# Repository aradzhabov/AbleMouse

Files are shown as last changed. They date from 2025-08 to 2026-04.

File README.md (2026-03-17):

# AbleMouse Ecosystem 

> English | [Chinese](README.cn.md) | [Russian](README.ru.md) | 🌍 Help us translate! Make the project global.

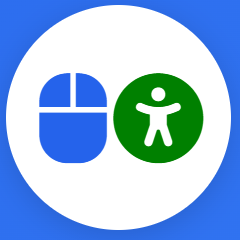
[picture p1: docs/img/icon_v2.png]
AbleMouse Demo
[//]: # ( )

## ✨ Open-source alternative to solutions like **MouthPad**, **eye-trackers**, or even complex systems like **Neuralink**.

> ❤️Our solution gives people with physical disabilities the power to go online — and in doing so, rediscover their self-worth, confidence, and dignity.

> [AbleMouse was selected by the ✨Product Hunt (PH) editors and received the "Featured" status. This is a significant honor. It means the world to me that people voted with their hearts.](https://www.producthunt.com/products/ablemouse-control-with-tongue-or-touch/launches)

### 🚀 [News]
>
   > AbleMouse now consists of several sub-products designed to assist users [based on their individual physical abilities](#product-compatibility-with-user-physical-abilities).
> 
> 🔥 Jan 2026  - [AbleMouse Beyond Switch](AbleMouse_Beyond_Switch_edition.md) - Control your entire PC with a single gesture. A uniquely simple approach.
> 
   > December 2025 - [AbleMouse AI Edition](AbleMouse_AI_edition.md)  is introduced. Cursor control using computer vision!
> 
   > November 2025 - [MouseCommander (win)](https://github.com/aradzhabov/AbleMouse/blob/main/src/windows/auto_hot_key/README.md) is introduced. Mouse Gesture-Controlled Quick Actions. +  [A new 3D-printable case for the ESP32 board is available](https://github.com/aradzhabov/AbleMouse/blob/main/AbleMouseDIY.md#news--november-27-2025)
> 
   > September 2025 - [AbleMouse DIY Edition](AbleMouseDIY.md) is introduced. Control your mouse with just tongue movements or simple touches on fully customizable pedals with any available body part. 
> 
---

# Product Compatibility with User Physical Abilities

> 🛈 AbleMouse now consists of several sub-products designed to assist users based on their individual physical abilities. Below is a table to help you navigate the available options and find the most suitable one for your needs. Each product name includes a link to its dedicated page with detailed information.

| User's Physical Challenge                                | Usable Body Part(s)                                   | Recommended Product                                                                                                                                          | Release Status    | Compatible Operating Systems                                                      |
|----------------------------------------------------------|-------------------------------------------------------|--------------------------------------------------------------------------------------------------------------------------------------------------------------|-------------------|-------------------------------------------------------------------------------------|
| Complete paralysis of body and head                      | Can use tongue                                        | **[AbleMouse DIY Edition](AbleMouseDIY.md)**                                                                                                                 | Already available | Windows, macOS, iOS, iPadOS, Unix (Ubuntu), Android                                |
| Complete paralysis of body and head                      | Imagine a person who is completely paralyzed (both body and head) and is also unable to speak. In the specific case I am referring to, the individual only had access to a single micro-movement — he could only slightly open his mouth.                                                  | **[AbleMouse Beyond Switch edition](AbleMouse_Beyond_Switch_edition.md)**                                                                                                                      | 🔥Jan 2026        | Windows                                                                             |
| Complete body paralysis                                  | Can tilt, turn, or nod head; eyes or mouth functional | **[AbleMouse AI Edition](AbleMouse_AI_edition.md)**                                                                                                          | Already available | Windows, macOS (Unix/Ubuntu support possible — requires testing)                   |
| Poor head control (e.g., due to cerebral palsy)          | Can move other body parts (even imprecisely)          | **[AbleMouse DIY Edition](AbleMouseDIY.md)**                                                                                                                 | Already available | Windows, macOS, iOS, iPadOS, Unix (Ubuntu), Android                                |
| Any of the above conditions                              | —                                                     | **[MouseCommander (win)](https://github.com/aradzhabov/AbleMouse/blob/main/src/windows/auto_hot_key/README.md) as an additional tool to any above products** | Already available | Windows                                                                             |

## Who Is It For?
> This solution is designed for users who, for various reasons, are unable to operate a mouse effectively.
- People with **ALS** (Amyotrophic Lateral Sclerosis), cerebral palsy, spinal cord injuries, muscular dystrophy
- Those undergoing **rehabilitation after stroke**
>...and for those who want to help.
- **Parents, teachers, and activists** who want to provide affordable help
- Anyone who believes **assistive technology should be a right, not a privilege**

## How to Contribute

We welcome contributions! Here's how you can help:

1. **Spread the Word** - Share with communities who might benefit
2. **Improve Documentation** - Help make guides clearer and more accessible. Help translate to make this project available to non-English speakers.
3. **Develop Features** - Implement new functionality or platform support
4. **Test and Report** - Try building and report any issues

## Support
- aradzhabov@gmail.com
- [LinkedIn](https://www.linkedin.com/in/aradzhabov/)

## License

MIT License - see [LICENSE](LICENSE) file for details.

---

### Connect With Us



**#Accessibility #AssistiveTech #OpenSource #DIY #Innovation #MouthPad #eye-tracker #Neuralink**

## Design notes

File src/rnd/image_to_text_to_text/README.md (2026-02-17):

# talk2cam: Ask Your Camera Anything. Completely locally

**Live Camera Feed QA. Vision-to-Text: Conversing with Reality in Real-Time**




>▶️[Video talk2cam](https://youtu.be/8lIvBt9HPiM)
---

## Special Thanks
Special thanks to the **[Alibaba Cloud team](https://www.alibabacloud.com/)** for supporting the [AbleMouse project](https://github.com/aradzhabov/AbleMouse/tree/main), which helps make the world more accessible for people with disabilities, and of course for their excellent open-weight models.

---

## About The Project

I've been experimenting with integrating vision-capable language models with live camera streams. The result? An interactive system that can:

- Process real-time video frames
- Answer natural language questions about the scene
- Adapt to new instructions on the fly

This opens up possibilities for:
- 👁️ Assistive technology for visually impaired
- 🏠 Real-time scene understanding
- 🤝 Interactive AI companions
- 📹 Smart surveillance systems

---

## 🚀 How to Run

### 1. Install [llama.cpp](https://github.com/ggml-org/llama.cpp)

There are multiple ways to do this. The simplest is to download a pre-compiled version for your hardware.

For example, I downloaded from [llama.cpp releases](https://github.com/ggml-org/llama.cpp/releases):
- `Windows x64 (CUDA 12)`
- `CUDA 12.4 DLLs`

- **Note 1:** Check your CUDA version by running `nvidia-smi` and looking at the top right corner.
- **Note 2:** If using GPU, copy files from `CUDA 12.4 DLLs` into the `Windows x64 (CUDA 12)` folder.
- **Note 3:** Without GPU everything still works, but you'll need to set a 10+ second delay between frames (for larger models).

### 2. Choose a Model

Browse video-text-to-text models with GGUF format on Hugging Face:
👉 [Video-to-Text Models with llama.cpp support](https://huggingface.co/models?pipeline_tag=video-text-to-text&library=gguf&apps=llama.cpp&sort=downloads)

**You don't need to manually download models** - when you run llama-server, it will automatically download the specified model.

### 3. Start the Server

#### Without GPU: 
- llama-server -hf prithivMLmods/SAGE-MM-Qwen2.5-VL-7B-SFT_RL-GGUF:Q4_K_M

#### With GPU:

- llama-server -hf prithivMLmods/SAGE-MM-Qwen2.5-VL-7B-SFT_RL-GGUF:Q4_K_M -ngl 99

Why this model? I like this model because it's multilingual and answers questions very well.
👉 [SAGE-MM-Qwen2.5-VL-7B-SFT_RL-GGUF](https://huggingface.co/prithivMLmods/SAGE-MM-Qwen2.5-VL-7B-SFT_RL-GGUF) on Hugging Face

💻 For weaker computers:
Try this smaller model (I found it good at describing what it sees, but not as good at answering follow-up questions):
llama-server -hf ggml-org/SmolVLM2-500M-Video-Instruct-GGUF:Q8_0

👉 [SmolVLM2-500M-Video-Instruct-GGUF](https://huggingface.co/ggml-org/SmolVLM2-500M-Video-Instruct-GGUF)
 
### 4. Run Camera Llama
[talk2cam.py](./talk2cam.py)

How to Use
- Start - Click "▶ Start" to begin camera capture
- Ask - Type your question in the instruction box
- Settings - Click "⚙ Settings" to adjust server URL, image size, and interval

⚙️ Configuration Options
- Server URL	Where llama.cpp server is running (default: http://localhost:8080)
- Camera ID	Which camera to use (0 = built-in, 1 = external)
- Interval	Milliseconds between frame captures
- Image Size	Resize images before sending (smaller = faster)
- Instruction	What to ask the model about each frame

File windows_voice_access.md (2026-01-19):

### Enabling Voice Access

1. Go to Windows **Settings > Accessibility > Speech**.
2. Toggle the **Voice access** switch to **On**.

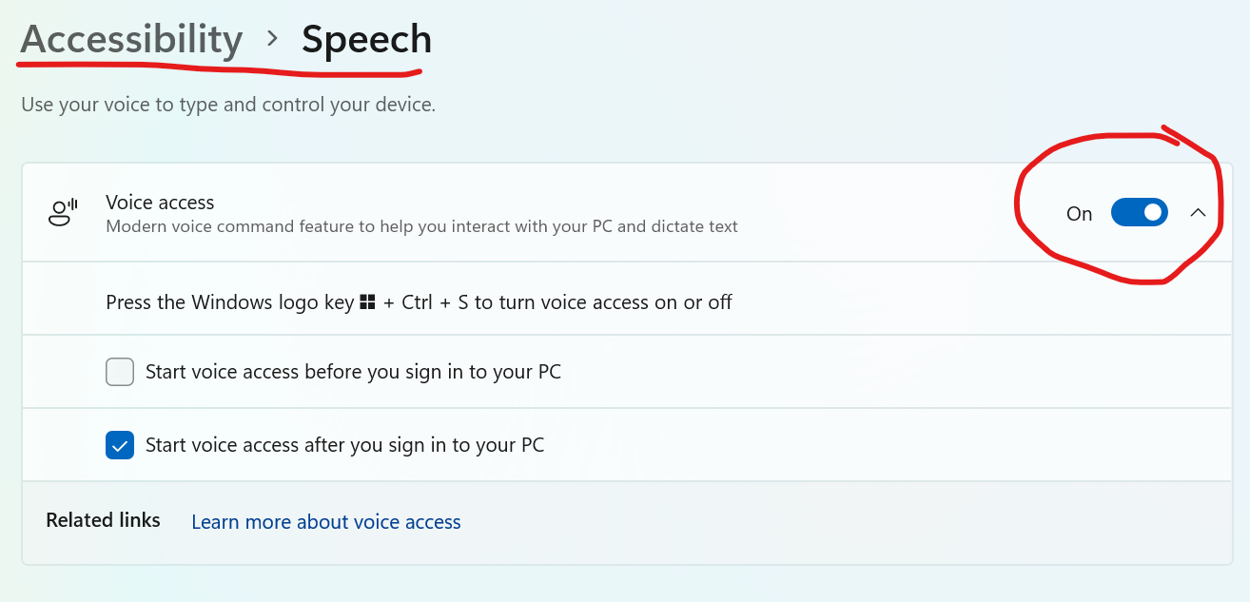
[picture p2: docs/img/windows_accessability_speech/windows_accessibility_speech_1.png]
Voice Access Settings


### Configuring Audio Input

Once enabled, the Voice Access bar will appear at the top of your screen. To route the audio correctly, follow these steps:

1. Click on the **Settings** (gear icon) on the Voice Access bar.
2. Under **Select default microphone**, choose **CABLE Output (VB-Audio Virtual Cable)**.
3. Finally, switch the mode from **Sleep** to **Active** by clicking the microphone icon on the left side of the bar.

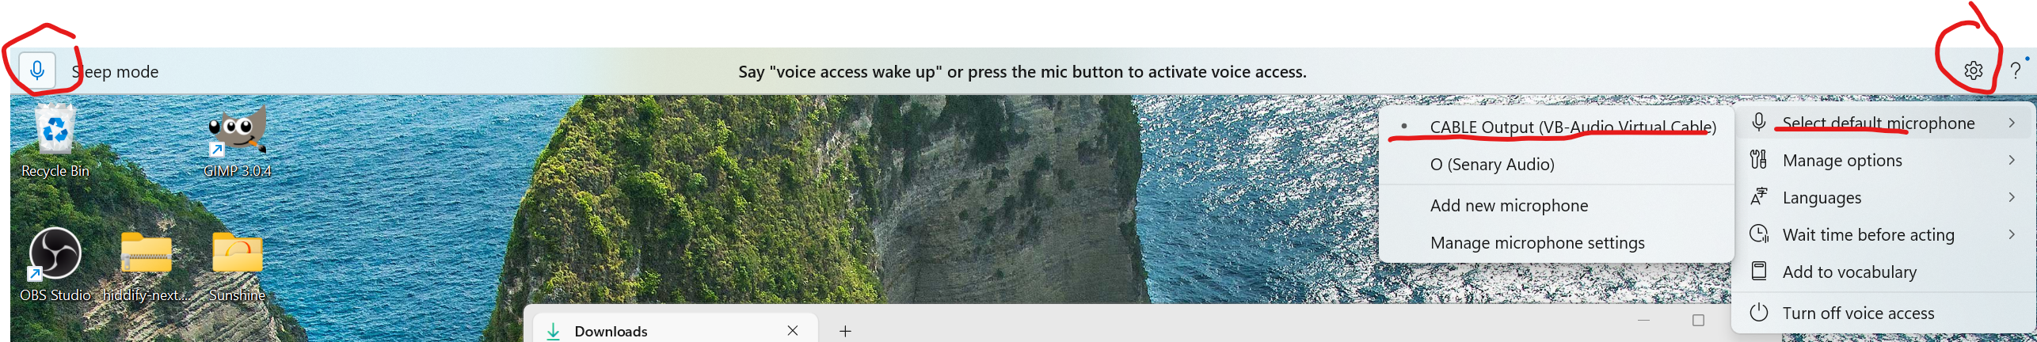
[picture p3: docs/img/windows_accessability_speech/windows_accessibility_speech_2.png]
Voice Access Configuration


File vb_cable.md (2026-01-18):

# VB-Cable Installation and Setup

> **Note:** VB-CABLE is distributed as  ([**Donationware**](https://vb-audio.com/Services/licensing.htm)). While it is free to download and use for personal purposes, a donation or license purchase is expected if you find the software useful or use it professionally. You can support the developer directly at the [VB-Audio Webshop](https://shop.vb-audio.com/en/win-apps/11-vb-cable.html).

### Why is this required?
VB-CABLE is a important component that allows the audio commands sent by the server to reach the **Windows Speech Control**. Without this setup, the system will "play" the audio, but Windows will not "hear" it as an input command.

---

### Step-by-Step Instructions

#### 1. Download and Install
* Download the driver pack: **VBCABLE_Driver_Pack45.zip** at [vb-audio.com/Cable/](https://vb-audio.com/Cable/).
* Extract the archive, run the setup as Administrator, and install.
* **Restart your computer** to complete the installation.

#### 2. Set Default Output
* Go to Windows **Settings > System > Sound**.
* In the **Output** section, select **CABLE Input (VB-Audio Virtual Cable)** as your output device.

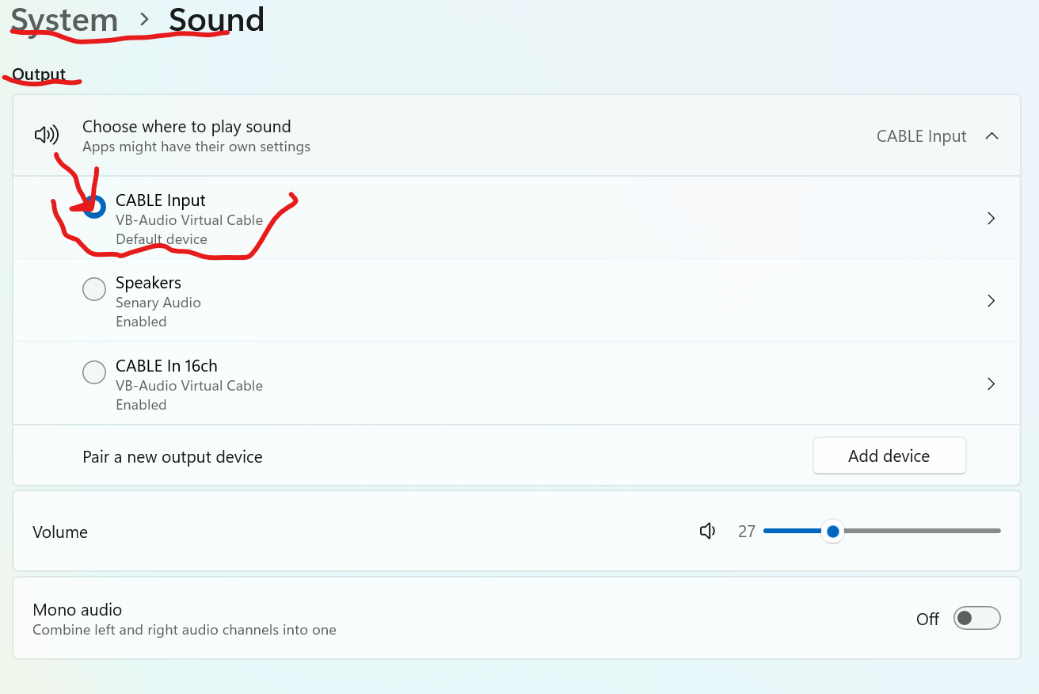
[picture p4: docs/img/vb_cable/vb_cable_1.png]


#### 3. Open Advanced Sound Settings
* Scroll down and click on **More sound settings** (or Sound Control Panel).

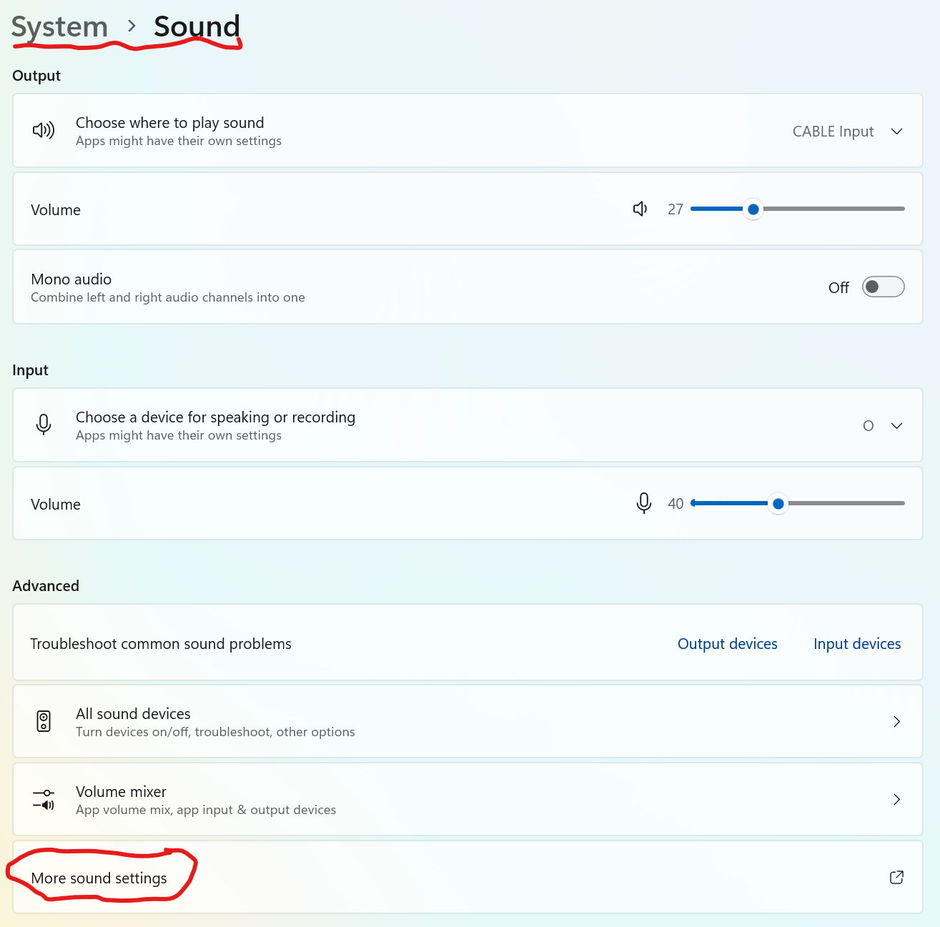
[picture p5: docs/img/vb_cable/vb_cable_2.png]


#### 4. Configure Audio Routing (Loopback)
* Switch to the **Recording** tab.
* Right-click on **CABLE Output** and select **Properties**.
* In the new window, go to the **Listen** tab.
* Check the box: **"Listen to this device"**.
* In the dropdown list under "Playback through this device", select the **speakers or headphones** you normally use for audio.

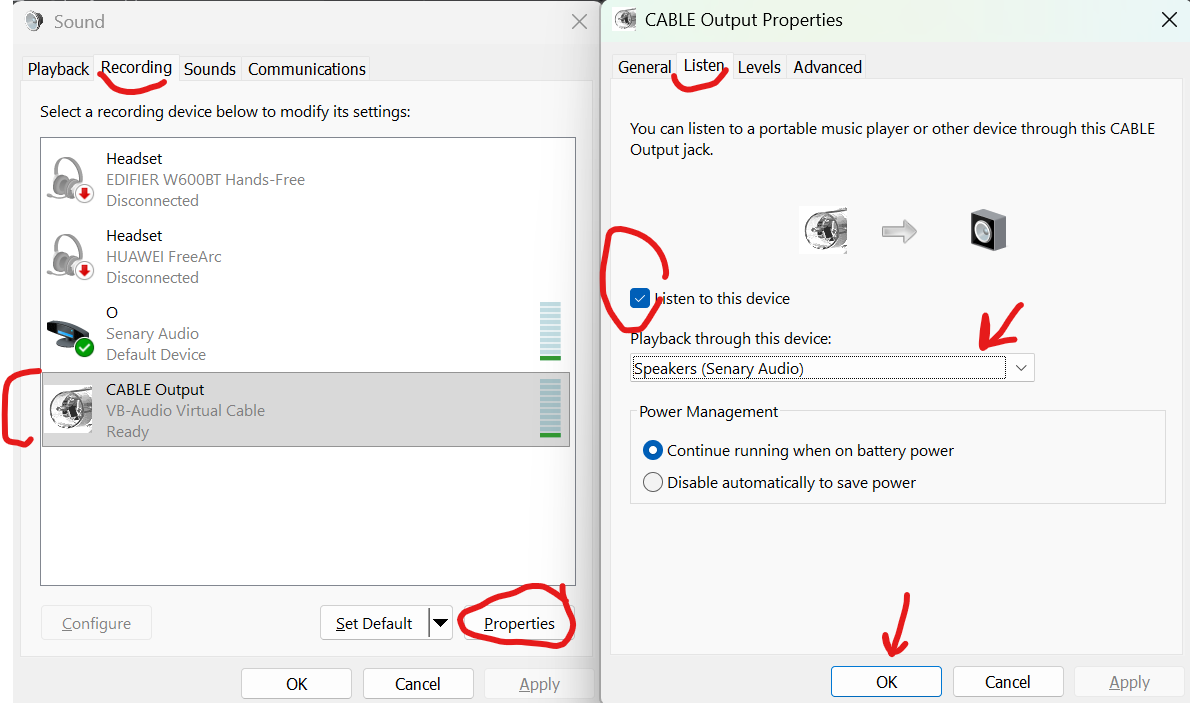
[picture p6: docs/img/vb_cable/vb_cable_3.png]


---

### Result
After following these steps, any audio played by the system will be routed through **VB-CABLE**, allowing Windows to "hear" and process the played commands.

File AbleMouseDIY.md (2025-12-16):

# AbleMouse DIV edition

> ❤️Control your mouse with just tongue movements or simple touches on fully customizable pedals with any available body part.
High-precision & affordable: the DIY (do it yourself) assistive solution

>▶️[Video AbleMouse](https://youtu.be/1eeg7Sakj_I)

### Assembly Steps
> [English](docs/en/assemble-guide.md) | 🌍 Help us translate! Make the project global.

## News  (November 27, 2025)
AbleMouse expands support to Unix, iOS, & iPadOS, making it compatible with all major OSes.
[A new 3D-printable case for the ESP32 board is available.](https://github.com/aradzhabov/AbleMouse/tree/main/3d_printer/models/esp32_box/variations/1)
The project also introduces [MouseCommander (win)](https://github.com/aradzhabov/AbleMouse/blob/main/src/windows/auto_hot_key/README.md), a new open-source component. It solves a key problem: how to use keyboard shortcuts and system tools without a physical keyboard or standart mouse. It opens a customizable menu via a gesture, enabling features like instant cursor "teleportation" via a screen preview, an on-screen keyboard and more.

## Key Features

| Feature | Description                                                                                                                                                                                                                                                                                                                |
|---------|----------------------------------------------------------------------------------------------------------------------------------------------------------------------------------------------------------------------------------------------------------------------------------------------------------------------------|
| **Universal Accessibility** | Helps both completely immobile users and those with minimal motor skills. You can use our solution with just your tongue, even with total paralysis.                                                                                                                                                                       |
| **Wireless Freedom** | Full Bluetooth control without cables                                                                                                                                                                                                                                                                                      |
| **Multi-Platform Support** | Works on Windows, macOS, iOS, iPadOS, unix(Ubuntu) and Android                                                                                                                                                                                                                                                             |
| **Plug & Play Simplicity** | For Windows, macOS, iOS, iPadOS, unix(Ubuntu) end-users: No additional software or drivers are required. Simply find and connect our device using your computer's standard Bluetooth settings—just like pairing a pair of wireless headphones. The moment it's connected, you can begin controlling your mouse.                                    
| **Ultra-Low Cost** | All components cost less than $10 USD                                                                                                                                                                                                                                                                                      |
| **Short Learning Curve** | The adaptation was startlingly fast—within 20 minutes, my control was precise and confident                                                                                                                                                                                                                                |
| **Open Source & hackable** | DIY. Assemble and customize it yourself in a garage, workshop, or makerspace. All instructions and code are openly available.                                                                                                                                                                                              
| **No Expert Needed** | You don't need to be an IoT expert to build it. In fact, the setup is so simple that you can easily find a helper in your immediate circle—be it a colleague from the IT department, a tech-savvy friend, or a student. It's all based on simple copy-paste operations, so no deep knowledge is required from them either. 

## Support
- aradzhabov@gmail.com
- [LinkedIn](https://www.linkedin.com/in/aradzhabov/)

## License

MIT License - see [LICENSE](LICENSE) file for details.

---

### Connect With Us



**#Accessibility #AssistiveTech #OpenSource #DIY #Innovation #MouthPad #eye-tracker #Neuralink**

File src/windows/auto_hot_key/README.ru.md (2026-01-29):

# MouseCommander — Быстрые действия, управляемые жестами мыши

> Этот подход был разработан в ответ на запросы людей с ограниченными возможностями, использующих Windows, чтобы упростить и ускорить их рабочий процесс. Он специально предназначен для тех, кто может управлять только указателем мыши (без использования обычной мыши) и не может пользоваться клавиатурой. Решение позволяет быстро перемещаться к нужным точкам экрана, вызывать экранный клавиатуру (OSK) и позиционировать курсор внутри неё, а также упрощает наведение на конкретные точки с помощью прицельной сетки.
> 
> Подход легко переводится на любой язык и расширяется дополнительными функциями по мере необходимости.
> 
> Ниже приведён подробный рабочий пример скрипта. Используя его как основу, вы можете разработать собственный жест и персонализированный набор доступных команд, которые наилучшим образом соответствуют вашим потребностям.

## Обзор
> ▶️ [пример вызова меню при использовании AbleMouse AI edition](https://rutube.ru/video/c27362a9037dbe7b9ceb7fb06f275b4c/?r=wd&t=69)
> 
> ▶️ [демонстрация возможностей](https://rutube.ru/video/83b28184f3693f3217fb0cab863da98a/)
> 
Скрипт автоматизации на основе жестов, распознающий движения мыши (влево → вправо) как пример для отображения панели быстрого доступа с различными системными функциями.

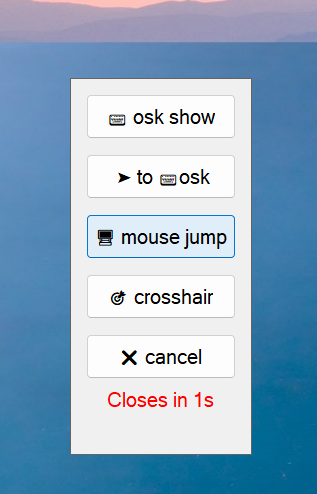
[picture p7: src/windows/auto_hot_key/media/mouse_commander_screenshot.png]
Скриншот


## Исходный код
[mouse_commander.ahk](./mouse_%D1%81ommander.ahk)

## Возможности
- Распознавание жестов мыши (движение влево → вправо)
- Панель быстрого доступа с настраиваемыми действиями
- **osk hide/show**: Переключение видимости экранный клавиатуры
- **osk to cursor**: вызов экранной клавиатуры и фокусировка курсора на ней
- **mouse jump**: Мгновенный переход указателя мыши в любую точку рабочего стола
- **crosshair**: Переключение прицельной сетки поверх экрана
- Возможность самостоятельно добавлять новые функции

## Настройки конфигурации

### Параметры жестов
```autohotkey
gestureTimeWindow := 1000  ; Временное окно распознавания жеста в миллисекундах
minDistance := 50          ; Минимальное расстояние перемещения в пикселях
maxPause := 300            ; Максимальная пауза между движениями
menuTimeout := 3000        ; Автозакрытие меню через 3 секунды
```

### Настройки горячих клавиш
```
oskToggleHotkey := "#^o"   ; Win+Ctrl+O — переключение видимости экранных клавиатур
mouseJumpHotkey := "#+d"   ; Win+Shift+D
crosshairHotkey := "#!p"   ; Win+Alt+P
```

### Установка (протестировано с AutoHotkey v2.0 и PowerToys 0.94)

```
Установите AutoHotkey v2.0
Установите PowerToys 0.94
Сохраните скрипт с расширением .ahk
Запустите скрипт
```

### Использование

```
Базовый жест
Выполните движение мыши ВЛЕВО (> 50 пикселей)
Немедленно выполните движение ВПРАВО (> 50 пикселей)
Весь жест должен быть завершён в течение 1000 мс
```

### Опции панели быстрого доступа
```
osk hide/show: Переключение видимости экранных клавиатур
osk to cursor: Перемещение экранных клавиатур к курсору и фокусировка
mouse jump: Мгновенный переход указателя мыши в любую точку экрана
crosshair: Переключение прицельной сетки
Cancel: Закрыть меню
```

### Примечания
```
Скрипт автоматически определяет, запущена ли экранные клавиатуры
Все элементы интерфейса корректно уничтожаются для предотвращения утечек памяти
```

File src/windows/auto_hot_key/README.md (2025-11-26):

# MouseCommander - Mouse Gesture-Controlled Quick Actions

>This approach was developed in response to requests from people with disabilities who use Windows, to simplify and accelerate their workflow. It is especially designed for those who can only control a mouse pointer (without a regular mouse) and cannot use a keyboard. It enables quick movement to desired screen locations, calling the on-screen keyboard (OSK) and positioning the cursor within it, and simplifies aiming at specific points using crosshair assistance.
This approach can be easily extended with additional functions as needed.
> 
> Below is a detailed working example of a script. Using this as a foundation, you can design a custom gesture and a personalized set of available commands that best suit your needs.

## Overview
>▶️[demo](https://youtu.be/IWix3twlcew)
> 
A gesture-based automation script that recognizes mouse gestures (Left → Right) as an example to display a quick access panel with various system functions.



## Source
[mouse_commander.ahk](./mouse_сommander.ahk)

## Features
- Mouse gesture recognition (Left → Right movement)
- Quick access panel with customizable actions
- osk hide/show: Toggle on-screen keyboard visibility
- osk to cursor: Move OSK to cursor position and focus it
- mouse jump: Jump the mouse pointer quickly to anywhere on your desktop.
- crosshair: Toggle crosshair overlay
- you can add new features by yourself

## Configuration Settings

### Gesture Settings
```autohotkey
gestureTimeWindow := 1000  ; Gesture time window in milliseconds
minDistance := 50          ; Minimum movement distance in pixels
maxPause := 300            ; Maximum pause between movements
menuTimeout := 3000        ; Menu close timeout after 3 seconds
```

### Hotkey Settings
```autohotkey
oskToggleHotkey := "#^o"   ; Windows+Ctrl+O - toggles OSK visibility
mouseJumpHotkey := "#+d"   ; Windows+Shift+D
crosshairHotkey := "#!p"   ; Windows+Alt+P
```

## Installation (tested with AutoHotkey v2.0 and PowerToys 0.94)
1. Install [AutoHotkey v2.0](https://www.autohotkey.com/)
2. Install [PowerToys 0.94](https://github.com/microsoft/PowerToys/releases/tag/v0.94.0)
2. Save the script with `.ahk` extension
3. Run the script

## Usage

### Basic Gesture
1. Make a LEFT mouse movement (> 50px)
2. Immediately follow with a RIGHT movement (> 50px)
3. The entire gesture must be completed within 1000ms

### Quick Panel Options
- **osk hide/show**: Toggle on-screen keyboard visibility
- **osk to cursor**: Move OSK to cursor position and focus it
- **mouse jump**: Jump the mouse pointer quickly to anywhere on your desktop.
- **crosshair**: Toggle crosshair overlay
- **Cancel**: Close the menu

### Additional Controls
- **Pause**: Toggle gesture tracking on/off
- **Ctrl+Alt+I**: Show information panel
- **Escape**: Close active GUI window

## Technical Details

### Gesture Recognition
The script uses a state machine to track mouse movements:
- State 0: Waiting for initial movement
- State 1: Left movement detected
- State 2: Right movement completes the gesture

### Feedback System
- Visual tooltips provide gesture status feedback
- Countdown timer shows menu auto-close timing
- Color-coded indicators (gray → red) for time remaining

### GUI Management
- Always-on-top tool window
- Borderless design with custom styling
- Automatic positioning near cursor
- Timeout-based auto-destruction

## Customization
Modify the configuration section to:
- Adjust gesture sensitivity (`minDistance`, `maxPause`)
- Change menu timeout duration (`menuTimeout`, `countdownTime`)
- Customize hotkey combinations
- Add new menu options and corresponding functions

## Notes
- The script automatically detects if OSK is already running
- All GUI elements are destroyed properly to prevent memory leaks
- The pause feature allows temporary disabling of gesture recognition

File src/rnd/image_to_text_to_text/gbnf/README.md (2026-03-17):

* Ограничиваю модель двумя предложениями через настройки сервера
>llama-server -hf prithivMLmods/SAGE-MM-Qwen2.5-VL-7B-SFT_RL-GGUF:Q4_K_M -ngl 99 --grammar-file two_sentences.gbnf

>

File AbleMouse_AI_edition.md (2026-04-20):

# AbleMouse AI edition

> ❤️Control the mouse pointer using your face.
> 
> The code works under both Windows and Mac Os. Note: Unix/Ubuntu support possible — requires testing

>▶️[Video AbleMouse AI edition](https://youtu.be/AlqSVKt535Y)
> / [Source Code](src/ablemouse_ai_edition/able_mouse_ai_edition.py) / ▶️[initial setup](https://youtu.be/KCn4GMMQkxc)
> 
> Note: In the video demonstration for calling the on-screen keyboard in Windows, I used gesture recognition via [MouseCommander (win)](https://github.com/aradzhabov/AbleMouse/blob/main/src/windows/auto_hot_key/README.md) , which is also part of the AbleMouse project. <br> On macOS, there is no need to use MouseCommander, as the built-in keyboard with the "dwelling" setting enabled and customizable transparency levels is both convenient and does not clutter the interface with its presence.

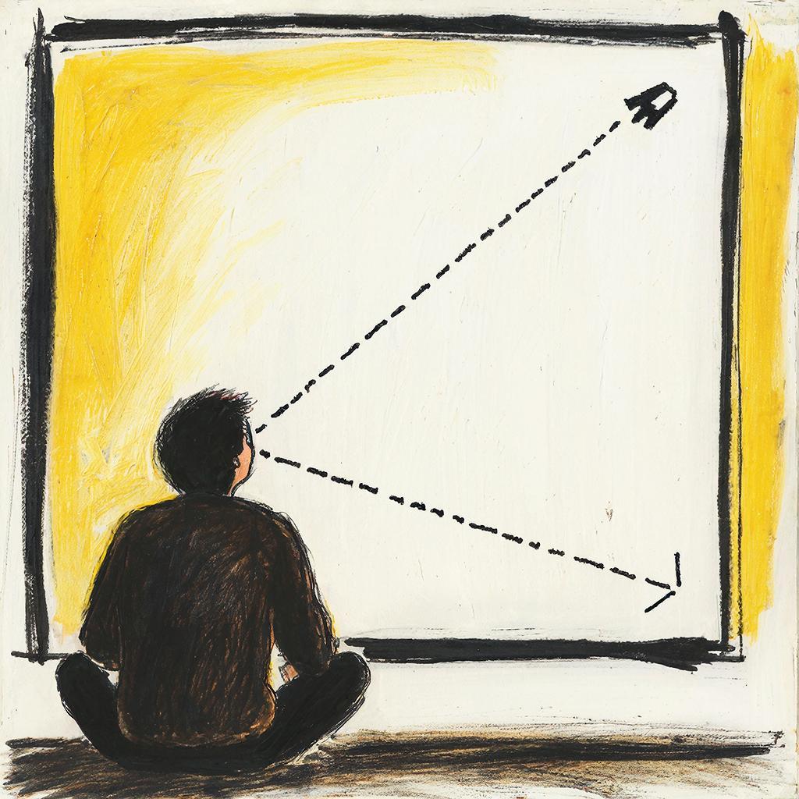
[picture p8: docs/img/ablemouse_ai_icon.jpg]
AbleMouse AI edition


An important aspect is that the solution is fully open-source and can be easily adapted to meet the needs of a specific individual.

To use AbleMouse AI edition, it is enough that you can turn and tilt your head, and use your eyes and mouth. 
The mouse pointer is positioned based on the direction of your nose, allowing you to work effectively even with very large screens.
macOS and Windows do not have such a solution built-in.
Another very important difference from other solutions is that your eyes remain free, as the tracking is based on the direction of your nose. This provides a much more natural feeling for us as humans. For example, solutions that require you to look at the point where you want to move the cursor demand significantly more effort and feel unnatural. An ordinary person using a hand-operated mouse can look anywhere—AbleMouse allows you to do the same.

A few notes on use and configuration:

*   To adapt the program for a specific person, you will need the assistance of someone with basic Python knowledge. In my opinion, a school student's level is sufficient.
    The solution itself is very simple and essentially consists of a single file where settings need to be adjusted for the specific user. Most parameters in the code are self-explanatory from their names, and in most cases, many of them do not need to be changed. I will describe the most important ones below. Please don't hesitate to write to me if you have any questions.

*   I recommend using an external webcam, as this allows for maximum comfort in screen positioning, especially for bedridden individuals.
    If you are using an external webcam, you need to set the `camera` parameter to a value other than 0 (usually this value is 1). The value 0 corresponds to the built-in camera in your laptop.

All camera settings are located in `able_mouse_ai_edition_config.json` under the `"main"` section:

```json
"main": {
    "camera": 0,
    ...
}   
```

*   `EYE_CLOSE_THRESHOLD` - Thresholds for determining closed eyes (distance between the upper and lower eyelashes).
    `MOUTH_OPEN_THRESHOLD` - Threshold for determining an open mouth (distance between the lips).
 
```commandline
"eye_and_mouth": {
    "eye_close_threshold": 0.005,
    "mouth_open_threshold": 0.004,
    ...
}

```

It is important to understand that these parameters greatly depend on the distance of the face from the camera and the camera itself. You also need to consider that, for example, when you tilt your head, the distance between the calculated points decreases due to projection. When you run the program, you can easily check its operation with your settings, as a window will open displaying each gesture. This window can also be used for training. The window will remain open while the program is running but can be hidden behind other applications. This does not affect the program's operation.

*   For Python developers: `Python 3.9-3.12`. To run the program, you will need to create a virtual environment (venv) and install just 3 packages:
    `opencv-python`, `mediapipe==0.10.21`, `pyautogui`
    After that, run [able_mouse_ai_edition.py](src/ablemouse_ai_edition/able_mouse_ai_edition.py). !!After launching, don't forget to properly [calibrate the camera position](https://youtu.be/KCn4GMMQkxc)!!

*   Overall, I also see the program as an educational moment. I think many students will be able to pick up something useful for themselves.
    The program itself is a maximally simplified, small slice from my R&D version from two years ago.

    I could have significantly simplified the code by using `sleep` instructions in more places instead of cooldowns, but my experience shows that these freezes are very noticeable and feel unnatural. I also intentionally did not publish a clean object-oriented version of the code, as it will be much easier for beginners to understand a version without OOP.

## Support
- aradzhabov@gmail.com
- [LinkedIn](https://www.linkedin.com/in/aradzhabov/)

## License

MIT License - see [LICENSE](LICENSE) file for details.

---

### Connect With Us



**#Accessibility #AssistiveTech #OpenSource #DIY #Innovation #MouthPad #eye-tracker #Neuralink**

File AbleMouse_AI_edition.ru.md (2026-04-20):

# AbleMouse AI edition

> ❤️ Управление курсором мыши с помощью лица. В точку по направлению, куда указывает нос, позиционируется курсор, а клики делаются глазами и ртом. Позиционирование происходит именно по направлению, т.е. экран может быть любого размера, но человеку никуда не нужно двигаться - нужно просто направить нос в точку, куда переместить курсор.
> 
> Код работает в Windows и macOS. Примечание: поддержка Unix/Ubuntu возможна, но требует тестирования.

>▶️ [Видео AbleMouse AI edition](https://rutube.ru/video/c27362a9037dbe7b9ceb7fb06f275b4c/)
> / [Исходный код](src/ablemouse_ai_edition/able_mouse_ai_edition.py) / ▶️ [Первоначальная настройка](https://youtu.be/KCn4GMMQkxc)
> 
> Примечание: В видеодемонстрации для вызова экранной клавиатуры в Windows я использовал распознавание жестов через [MouseCommander (win)](https://github.com/aradzhabov/AbleMouse/blob/main/src/windows/auto_hot_key/README.md), который также является частью проекта AbleMouse. <br> На macOS нет необходимости использовать MouseCommander, так как встроенная клавиатура с включенной функцией «ожидания» (dwelling) и настраиваемой прозрачностью очень удобна и не загромождает интерфейс.

AbleMouse AI edition

Важным аспектом является то, что это решение полностью открыто (open-source) и может быть легко адаптировано под нужды конкретного человека.

Для использования AbleMouse AI edition достаточно иметь возможность поворачивать и наклонять голову, а также задействовать глаза и рот. 
Курсор мыши позиционируется в зависимости от направления вашего носа, что позволяет эффективно работать даже с очень большими экранами. 
В macOS и Windows подобных встроенных решений нет. 

Еще одно очень важное отличие от других систем заключается в том, что ваши глаза остаются свободными, так как трекинг основан на направлении носа. Это обеспечивает гораздо более естественное ощущение для человека. Например, решения, требующие смотреть именно в ту точку, куда вы хотите переместить курсор, требуют значительно больше усилий и кажутся неестественными. Обычный человек, использующий ручную мышь, может смотреть куда угодно — AbleMouse позволяет делать то же самое.

### Несколько заметок по использованию и настройке:

*   Для адаптации программы под конкретного человека потребуется помощь кого-то с базовыми знаниями Python. На мой взгляд, уровня школьника будет достаточно. 
    Само решение очень простое и по сути состоит из одного файла, где нужно подправить настройки под конкретного пользователя. Большинство параметров в коде интуитивно понятны по их названиям, и во многих случаях их даже не придется менять. Ниже я опишу самые важные из них. Пожалуйста, не стесняйтесь писать мне, если у вас возникнут вопросы.

*   Я рекомендую использовать внешнюю веб-камеру, так как это обеспечивает максимальный комфорт в расположении экрана, особенно для лежачих больных. 
    Если вы используете внешнюю камеру, вам нужно установить параметр `camera` в значение, отличное от 0 (обычно это 1). Значение 0 соответствует встроенной камере ноутбука.

Все настройки можно изменить в  `able_mouse_ai_edition_config.json`:

```json
"main": {
    "camera": 0,
    ...
}   
```

*   `EYE_CLOSE_THRESHOLD` — пороги для определения закрытых глаз (расстояние между верхними и нижними ресницами).
    `MOUTH_OPEN_THRESHOLD` — порог для определения открытого рта (расстояние между губами).

```commandline
"eye_and_mouth": {
    "eye_close_threshold": 0.005,
    "mouth_open_threshold": 0.004,
    ...
}

Важно понимать, что эти параметры сильно зависят от расстояния лица до камеры и самой модели камеры. Также нужно учитывать, что, например, при наклоне головы расстояние между расчетными точками уменьшается из-за проекции. При запуске программы вы сможете легко проверить работу со своими настройками: откроется окно, отображающее каждый жест. Это же окно можно использовать для тренировки. Окно будет оставаться открытым во время работы программы, но его можно скрыть за другими приложениями — на работу это не влияет.

*   Для Python-разработчиков: `Python 3.9-3.12`. Для запуска программы нужно создать виртуальное окружение (venv) и установить всего 3 пакета: 
    `opencv-python`, `mediapipe==0.10.21`, `pyautogui`. 
    После этого запустите [able_mouse_ai_edition.py](src/ablemouse_ai_edition/able_mouse_ai_edition.py). !!После запуска не забудьте правильно [откалибровать положение камеры](https://youtu.be/KCn4GMMQkxc)!!

*   В целом, я рассматриваю эту программу и как образовательный момент. Думаю, многие студенты смогут почерпнуть здесь что-то полезное для себя. 
    Сама программа — это максимально упрощенный, небольшой «срез» из моей R&D версии двухлетней давности. 

    Я мог бы значительно упростить код, используя инструкции `sleep` вместо кулдаунов (cooldowns), но мой опыт показывает, что такие замирания очень заметны и ощущаются неестественно. Также я намеренно не публиковал чистую объектно-ориентированную версию кода, так как новичкам будет гораздо проще разобраться в версии без ООП.

## Поддержка
- aradzhabov@gmail.com
- [LinkedIn](https://www.linkedin.com/in/aradzhabov/)

## Лицензия

MIT License — подробности в файле [LICENSE](LICENSE).

---

### Свяжитесь с нами

[![Website](https://img.shields.io/badge/Website-Learn%20More-green)](https://aradzhabov.github.io/gagarin_data_labs/)

**#Accessibility #AssistiveTech #OpenSource #DIY #Innovation #MouthPad #eye-tracker #NeuralNetworks**

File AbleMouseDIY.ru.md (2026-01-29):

# AbleMouse DIV edition

## ✨ Проект с открытым исходным кодом — альтернатива таким решениям, как **MouthPad**, **айтрекеры**, или даже сложным системам вроде **Neuralink**.
> ❤️ Решение подойдёт для всех, кто по тем или иным причинам не может полноценно пользоваться мышью.

> Управляйте курсором мыши **движениями языка** или **простыми касаниями на полностью настраиваемые педали** любой доступной частью тела.
Высокоточное и доступное решение для ассистивных технологий, которое можно собрать своими руками (DIY).

>Мы помогаем людям с инвалидностью почувствовать себя ценными, уверенными и полноправными членами общества.

>▶️[Видеообзор AbleMouse](https://rutube.ru/video/931e70c2d8f6c1edf99c20dda61d8ad8/)
### Шаги сборки
> [Руководство по сборке](docs/ru/assemble-guide.ru.md)

## Новости (27 ноября 2025)
AbleMouse расширяет поддержку на Unix, iOS и iPadOS, становясь совместимым со всеми основными операционными системами. 
[Доступен новый корпус для платы ESP32, который можно напечатать на 3D-принтере.]((https://github.com/aradzhabov/AbleMouse/tree/main/3d_printer/models/esp32_box/variations/1))
Также в рамках проекта представлен новый компонент с открытым исходным кодом — [MouseCommander](https://github.com/aradzhabov/AbleMouse/blob/main/src/windows/auto_hot_key/README.ru.md) (для Windows). Он решает ключевую проблему: как использовать сочетания клавиш и системные инструменты без физической клавиатуры или стандартной мыши. Компонент открывает настраиваемое меню по жесту, предоставляя такие функции, как мгновенное «телепортирование» курсора с помощью предпросмотра экрана, экранную клавиатуру и многое другое.

## Ключевые особенности

| Особенность | Описание                                                                                                                                                                                                                                                                                                                                           |
|-------------|----------------------------------------------------------------------------------------------------------------------------------------------------------------------------------------------------------------------------------------------------------------------------------------------------------------------------------------------------|
| **Универсальная доступность** | Помогает как **полностью обездвиженным** пользователям, так и тем, у кого сохранены минимальные моторные навыки. Вы можете использовать наше решение даже при полном параличе, используя только язык.                                                                                                                                              |
| **Беспроводная свобода** | Полный контроль по Bluetooth без проводов                                                                                                                                                                                                                                                                                                          |
| **Поддержка нескольких платформ** | Работает на indows, macOS, iOS, iPadOS, unix(Ubuntu) и Android                                                                                                                                                                                                                                                                                     |
| **Простота Plug & Play** | Для конечных пользователей Windows, macOS, iOS, iPadOS, unix(Ubuntu): не требуется дополнительного программного обеспечения или драйверов. Просто найдите и подключите наше устройство, используя стандартные настройки Bluetooth вашего компьютера — точно так же, как вы подключаете беспроводные наушники. В момент подключения вы уже можете начать управлять курсором. |
| **Сверхнизкая стоимость** | Все компоненты стоят меньше $10 USD                                                                                                                                                                                                                                                                                                                |
| **Короткий период обучения** | Адаптация происходит поразительно быстро — (в моем случае) в течение 20 минут управление стало точным и уверенным                                                                                                                                                                                                                                  |
| **Открытый исходный код и возможность модификации** | Соберите и настройте его самостоятельно в гараже, мастерской или makerspace. Все инструкции и код открыты и доступны.                                                                                                                                                                                                                              |
| **Не нужно быть экспертом** | Вам не нужно быть экспертом в IoT, чтобы собрать его. На самом деле, setup настолько прост, что вы легко найдете помощника в своем ближайшем окружении — будь то коллега из IT-отдела, разбирающийся в технологиях друг или студент. Всё основано на простых операциях копирования-вставки, поэтому от них также не потребуется глубоких знаний.   |

## Поддержка
- aradzhabov@gmail.com
- [LinkedIn](https://www.linkedin.com/in/aradzhabov/)

## Лицензия
Лицензия MIT — подробности см. в файле [LICENSE](LICENSE).

---
### Свяжитесь с нами



**#Доступность #АссистивныеТехнологии #OpenSource #DIY #Инновации #MouthPad #Айтрекер #Neuralink**

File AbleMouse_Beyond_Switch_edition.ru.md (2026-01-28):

# AbleMouse Beyond Switch Edition
**Когда всё остальное бессильно, это работает.** 🦾
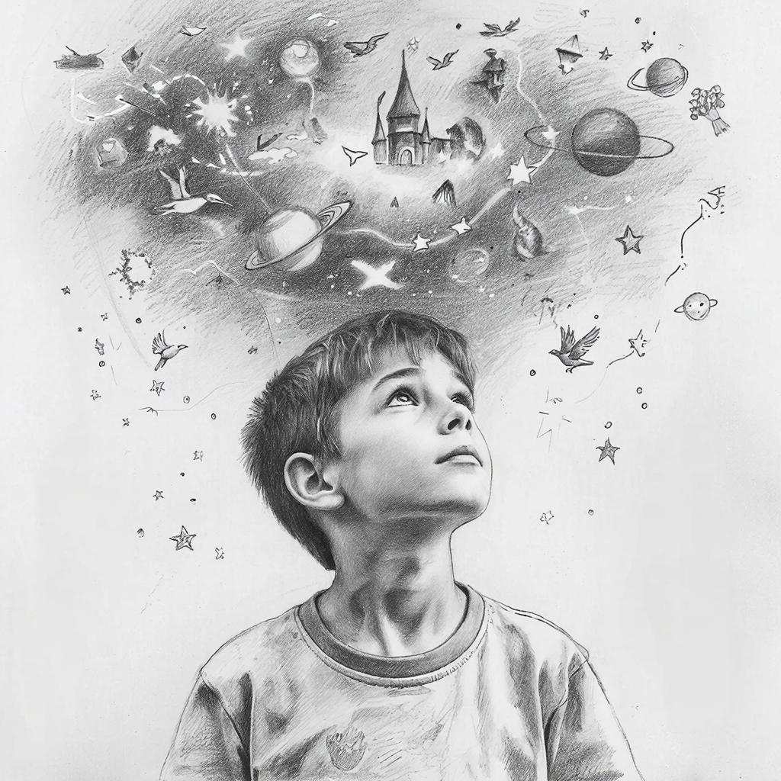
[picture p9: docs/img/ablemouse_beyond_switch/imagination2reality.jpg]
AbleMouse AI edition


🎞 **Видео-демонстрация :** [Смотреть на Rutube](https://rutube.ru/video/000e3cc6ab1bcda3238397a89fb534ff/)👆

Представьте **человека, который полностью парализован (тело и голова)** и при этом **не может говорить**. В конкретном случае, о котором я говорю, человеку было доступно лишь одно микродвижение — он мог лишь слегка приоткрыть рот.

🕊️ Я разработал решение, которое помогло человеку с такими серьезными ограничениями вернуться в цифровой мир и восстановить полный контроль над компьютером. Этот метод более естественен и гибок, чем традиционные подходы «Switch Control» (например, реализованные в macOS). <br>Я делюсь этой разработкой, потому что она способна изменить многие жизни.

❤️ Буду глубоко признателен, если вы поделитесь этим проектом с теми, кто в нем нуждается, или на специализированных форумах.

---

### ⚙️ Технические детали

🔹 **Принцип управления:** Система основана на иерархическом меню, которое циклически переключает элементы. Как только пользователь видит нужную команду, он подает сигнал (то самое микродвижение), и действие выполняется.

🔹 **Любой сенсор:** В текущей версии компьютерное зрение через стандартную веб-камеру фиксирует микродвижение рта. Однако архитектура позволяет подключить абсолютно любой входной сигнал или датчик. Вам просто нужно отправить команду на сервер приложения через **протокол TCP**.

🔹 **Преодоление языковых барьеров:** Интерфейс полностью настраиваемый и может быть переведен на любой язык. Ограничения Windows по поддерживаемым языкам ввода обходятся автоматически — пользователь видит свой родной язык, а система корректно интерпретирует команды.

🔹 **Гибкость:** Серверная часть позволяет построить меню любой сложности, адаптированное под конкретные задачи и физические возможности человека.

✨ **Основная концепция:** По сути, система создает интерфейс взаимодействия с компьютером для людей с экстремальными физическими ограничениями. Более того, она делает возможным голосовое управление Windows даже для тех, кто не может говорить.

---
# Компоненты, установка и запуск

> **Примечание:** Код AbleMouse Beyond Switch является открытым, бесплатным и распространяется под лицензией MIT. Однако для маршрутизации аудио я использую драйвер VB-CABLE. <br>VB-CABLE распространяется как Donationware. Хотя его можно скачать и использовать бесплатно, ожидается пожертвование или покупка лицензии, если вы считаете его полезным или используете профессионально.
> Вы можете поддержать разработчика по следующей ссылке на [vb-audio](https://shop.vb-audio.com/en/win-apps/11-vb-cable.html)

## Компоненты программы, их назначение и настройка

1.  **[menu_config.py](src/ablemouse_beyond_switch_edition/menu_config.py)** — Конфигурация меню, отображаемого в приложении. Это своего рода конструктор, который можно адаптировать под нужды конкретного человека.
2.  **[app_config.py](src/ablemouse_beyond_switch_edition/app_config.py)** — Настройки приложения.
3.  **[main.py](src/ablemouse_beyond_switch_edition/main.py)** — Основной компонент, реализующий пользовательский интерфейс (UI) и логику сервера.
    *   Любое разработанное вами приложение, способное отправлять команды через TCP, может выступать в роли клиента.
    *   **Создание Python venv и настройка**
        * Если вы используете AbleMouse AI Edition в качестве клиента (см. шаг 4 ниже), необходимо использовать `Python 3.9–3.12`.
        * Помимо требований, указанных в установке AbleMouse AI Edition, в вашей виртуальной среде должен быть установлен пакет: `pygame`.
  *   В [app_config.py](src/ablemouse_beyond_switch_edition/app_config.py) установите значения для вашей конфигурации:
      *   `SERVER_CONFIG`
      *   `UI_CONFIG.highlight_interval` — этот параметр управляет скоростью чередования пунктов меню. Его нужно настроить под конкретного человека (чтобы у него было достаточно времени на реакцию).

4.  В качестве клиента можно использовать любое ваше приложение, способное связываться с сервером по протоколу TCP.
    *   4.1 В демонстрационном видео я использовал **AbleMouse AI Edition** в качестве клиента. Установка и настройка должны выполняться согласно руководству [AbleMouse AI Edition Setup](AbleMouse_AI_edition.md).
    * 4.2 В исходном коде [able_mouse_ai_edition.py](src/able_mouse_ai_edition/able_mouse_ai_edition.py) установите переменные:
      * 4.2.1 `USE_MENU_SYSTEM` = True
      * 4.2.2 Если вы измените хост и порт для сервера AbleMouse Beyond Switch в [main.py](src/ablemouse_beyond_switch_edition/main.py), их необходимо внести в переменные `MENU_HOST` и `MENU_PORT`.
      * 4.2.3 Также рекомендуется немного увеличить значение `MOUTH_OPEN_THRESHOLD` по сравнению с тем, что было установлено на шаге 4.1. Например, в моей конфигурации я использую `0.002` при независимом использовании AbleMouse AI Edition и `0.008` при совместном использовании с AbleMouse Beyond Switch.

5.  **Установите драйвер виртуального аудиоустройства VB-CABLE от VB-Audio Software.**
    *   Инструкции по установке и настройке по ссылке: [(en) vb_cable.md](vb_cable.md)

6.  **Запустите «Голосовое управление» Windows (Voice Access)**
    *   Windows Voice Access используется для выполнения голосовых команд, генерируемых основным компонентом.
    *   Инструкция по настройке: [(en) windows_voice_access.md](windows_voice_access.md)

7.  **Запуск приложения**
    1.  Запустите сервер: выполните [main.py](src/ablemouse_beyond_switch_edition/main.py)
    2.  Запустите клиент: [able_mouse_ai_edition.py](src/able_mouse_ai_edition/able_mouse_ai_edition.py).
    
8. **Начало сессии**
<br>Кликните по заголовку окна приложения, где запущено меню. Теперь полностью положитесь на AbleMouse Beyond Switch Edition. Уберите физическую мышь в сторону и выполняйте все задачи, используя только управление Beyond Switch.

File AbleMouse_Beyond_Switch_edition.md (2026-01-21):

# AbleMouse Beyond Switch Edition
**When All Else Fails, This Works.** 🦾
AbleMouse AI edition

🎞 **Video Demonstration :** [Watch on YouTube](https://youtu.be/1zWn1Ha5-U0)👆

Imagine a **person who is completely paralyzed (both body and head)** and is also **unable to speak**. In the specific case I am referring to, the individual only had access to a single micro-movement — he could only slightly open his mouth.

🕊️ I have developed a solution that helped a person with such a severe disability return to the digital world and regain full control of his computer. This method is more natural and flexible than traditional "Switch Control" approaches (like those implemented in macOS). <br>I am sharing this development because it has the potential to change many lives.

❤️ I would be deeply grateful if you could share this project with those in need or on specialized community forums.

---

### ⚙️ Technical Details

🔹 **Control Principle:** The system is based on a hierarchical menu that cyclically cycles through items. As soon as the user sees the desired command, they provide a signal (that specific micro-movement), and the action is executed.

🔹 **Any Sensor:** In the current version, computer vision via a standard webcam detects the mouth's micro-movement. However, the architecture allows for the connection of absolutely any input signal or sensor. You simply need to send a command to the application server via the **TCP protocol**.

🔹 **Breaking Language Barriers:** The interface is fully customizable and can be translated into any language. Windows' limitations on supported input languages are bypassed automatically — the user sees their native language, while the system correctly interprets the commands.

🔹 **Flexibility:** The server component allows you to build a menu of any complexity, tailored to the specific tasks and physical capabilities of the individual.

✨ **The Core Concept:** Essentially, the system creates a computer interaction interface for those with extreme physical limitations. Furthermore, it enables Windows voice control even for individuals who cannot speak.

---
# Components, Setup, and Launch

> **Note:** The AbleMouse Beyond Switch code is open sourced and free and distributed under the MIT license. However, to provide audio routing, I use the VB-CABLE driver. <br>VB-CABLE is distributed as Donationware. While it is free to download and use, a donation or license purchase is expected if you find it useful or use it professionally.
> You can support the developer using the following link to [vb-audio](https://shop.vb-audio.com/en/win-apps/11-vb-cable.html)

## Program Components, Their Purpose, and Configuration

1.  **[menu_config.py](src/ablemouse_beyond_switch_edition/menu_config.py)** - Configuration for the menu displayed in the application. It's a kind of constructor that can be adapted to an individual's needs.
2.  **[app_config.py](src/ablemouse_beyond_switch_edition/app_config.py)** - Application settings.
3.  **[main.py](src/ablemouse_beyond_switch_edition/main.py)** - The main component implementing the UI and server logic.
    *   Any application you develop that can send commands via TCP can act as a client.
    *   **Creating a Python venv and Setup**
        * If you are using AbleMouse AI Edition as a client (see step 4 below), you must use `Python 3.9–3.12`
        * Beyond the requirements listed in the AbleMouse AI Edition Setup, the following packages need to be installed in your virtual environment: `pygame`
  *   In [app_config.py](src/ablemouse_beyond_switch_edition/app_config.py), set the values for your configuration:
      *   `SERVER_CONFIG`
      *   `UI_CONFIG.highlight_interval` - This parameter controls the speed at which menu items alternate. It needs to be adjusted for the specific person you are helping (so they have enough time to react).

4.  Any custom application you develop that can communicate with the server via the TCP protocol can be used as a client.
    *   4.1 In the demonstration video, I used **AbleMouse AI Edition** as the client. Installation and configuration must be performed according to the [AbleMouse AI Edition Setup](AbleMouse_AI_edition.md) guide.
    * 4.2 In the source code [able_mouse_ai_edition.py](src/ablemouse_ai_edition/able_mouse_ai_edition.py), set the variable:
      * 4.2.1 `USE_MENU_SYSTEM` = True
      * 4.2.2  If you change the host and port for the AbleMouse Beyond Switch server [main.py](src/ablemouse_beyond_switch_edition/main.py), you must enter them into the `MENU_HOST` and `MENU_PORT` variables.
      * 4.2.3   It is also recommended to slightly increase the value of `MOUTH_OPEN_THRESHOLD` from what was set in step 4.1. For example, in my configuration I use `0.002` when using AbleMouse AI Edition independently and `0.008` when using it together with AbleMouse Beyond Switch.

5.  **Install the VB-CABLE Virtual Audio Device driver by VB-Audio Software.**
    *   Installation and setup instructions via the link: [vb_cable.md](vb_cable.md)

6.  **Launch Windows Accessibility Speech (Voice Access)**
    *   Windows Voice Access is used to execute the voice commands generated by the core component.
    *   Setup instructions: [windows_voice_access.md](windows_voice_access.md)

7.  **Launching the Application**
    1.  Start the Server: run [main.py](src/ablemouse_beyond_switch_edition/main.py)
    2.  Start the Client: [able_mouse_ai_edition.py](src/ablemouse_ai_edition/able_mouse_ai_edition.py).
    
8. **Start Session**
<br>Click on the title bar of the application window where the menu is running. Now, rely entirely on AbleMouse Beyond Switch Edition. Put your physical mouse aside and complete all tasks using only the Beyond Switch controls.

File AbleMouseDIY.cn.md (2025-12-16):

>A heartfelt thank you to Alex (canvaszhy@foxmail.com) for his incredible generosity and kindness in providing translation support. His help was truly invaluable! ❤️
# AbleMouse DIV edition

[//]: # ( )

## ✨✨ 一款类似于 **MouthPad（舌控口腔垫）**、**eye-trackers（眼动追踪设备）** ，甚至是 **Neuralink（脑机接口）** 这样复杂系统的平替方案
> ❤❤️ 仅需舌尖微动，或使用身体任意部位轻触自制的触控板，即可控制鼠标。高精度且高性价比：DIY（自己动手实现）的辅助控制解决方案

>▶️[观看 AbleMouse 演示视频](https://youtu.be/1eeg7Sakj_I)

### 组装教程
> [英文版](docs/en/assemble-guide.md) | ✋✋诚邀您协助翻译，惠及全球用户✋✋

## News  (November 27, 2025)
AbleMouse expands support to Unix, iOS, & iPadOS, making it compatible with all major OSes.
[A new 3D-printable case for the ESP32 board is available.](https://github.com/aradzhabov/AbleMouse/tree/main/3d_printer/models/esp32_box/variations/1)
The project also introduces [MouseCommander (win)](https://github.com/aradzhabov/AbleMouse/blob/main/src/windows/auto_hot_key/README.md), a new open-source component. It solves a key problem: how to use keyboard shortcuts and system tools without a physical keyboard or standart mouse. It opens a customizable menu via a gesture, enabling features like instant cursor "teleportation" via a screen preview, an on-screen keyboard and more.

## 核心功能

| 特性 | 描述                                                              |
|---------|-----------------------------------------------------------------|
| **普适性无障碍支持** | 同时满足完全失能用户与残存运动功能用户的需求。即使高位截瘫，仅凭舌尖动作也能操控                        |
| **无线自由体验** | 蓝牙连接操控，无需线缆                                                     |
| **跨平台兼容** | 支持Windows（Windows电脑）、iOS、iPadOS、 unix(Ubuntu)、macOS（苹果电脑）及 Android（安卓手机）操作系统             |
| **即连即用** | Windows/macOS用户无需额外驱动：通过系统蓝牙设置配对设备（就像您使用蓝牙连接无线耳机一样简单），配对成功即可立即使用 |
| **超低成本** | 全部组件成本低于10美元（约合人民币70元，不同国家/地区可能因为工业体系完善度不同而价格有所差异，但依旧是非常便宜的）    |
| **快速上手** | 仅需20分钟，即可理解并且精准控制，快速建立您的自信                                      |
| **开源可定制** | 您可以在车库、车间甚至是卧室完成组装，并且可以发挥您的创意自行微调，所有代码与教程完全开源                   |
| **零门槛构建** | 无需专业背景：IT同事、技术爱好者甚至是学生均可自主完成，全程按照我们提供的教程即可                      |

## 适用人群
> 专为无法有效操作传统鼠标的用户设计
- 例如罹患 **ALS（渐冻症）**、脑瘫、脊柱损伤、肌营养不良症的患者
- **中风康复期**人群
>...同时面向爱心援助者
- 希望为他人提供平价辅助方案的**家长、教师及公益人士**
- 认同 **辅助触控技术应为人权而非特权** 的每一位倡导者

## 参与贡献
诚邀您共同助力：

1. **传播推广** - 分享给潜在受益群体
2. **文档优化** - 完善指南可读性，协助多语言翻译
3. **功能开发** - 拓展新功能或其他平台支持
4. **测试反馈** - 亲自搭建一套我们的设备并提交改进意见

## 支持方式
- 📧📧 技术支持邮箱：aradzhabov@gmail.com

## 许可协议

MIT 许可证 - 详见 [LICENSE](LICENSE) 文件

---

### 联系我们

[](https://aradzhabov.github.io/gagarin_data_labs/)

**#无障碍设计 #辅助科技 #开源项目 #DIY #科技革新 #MouthPad #eye-tracker #Neuralink**

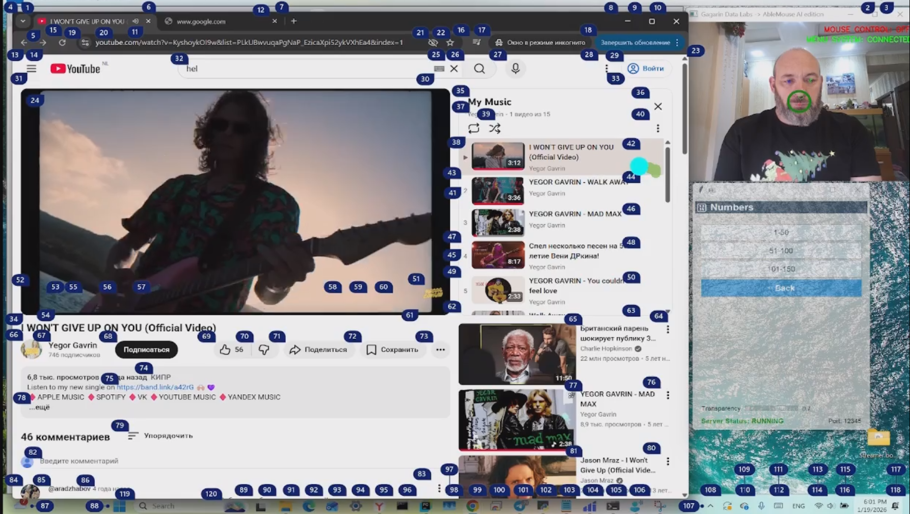
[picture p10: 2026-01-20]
docs/img/ablemouse_beyond_switch/ambs_demo_s_shot_numbers.png

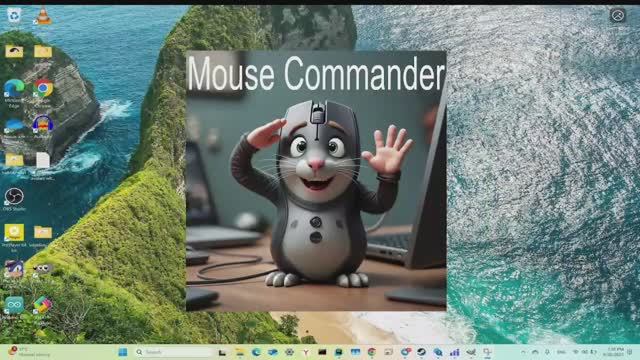
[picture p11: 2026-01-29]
src/windows/auto_hot_key/media/MouseCommander_baner.jpg

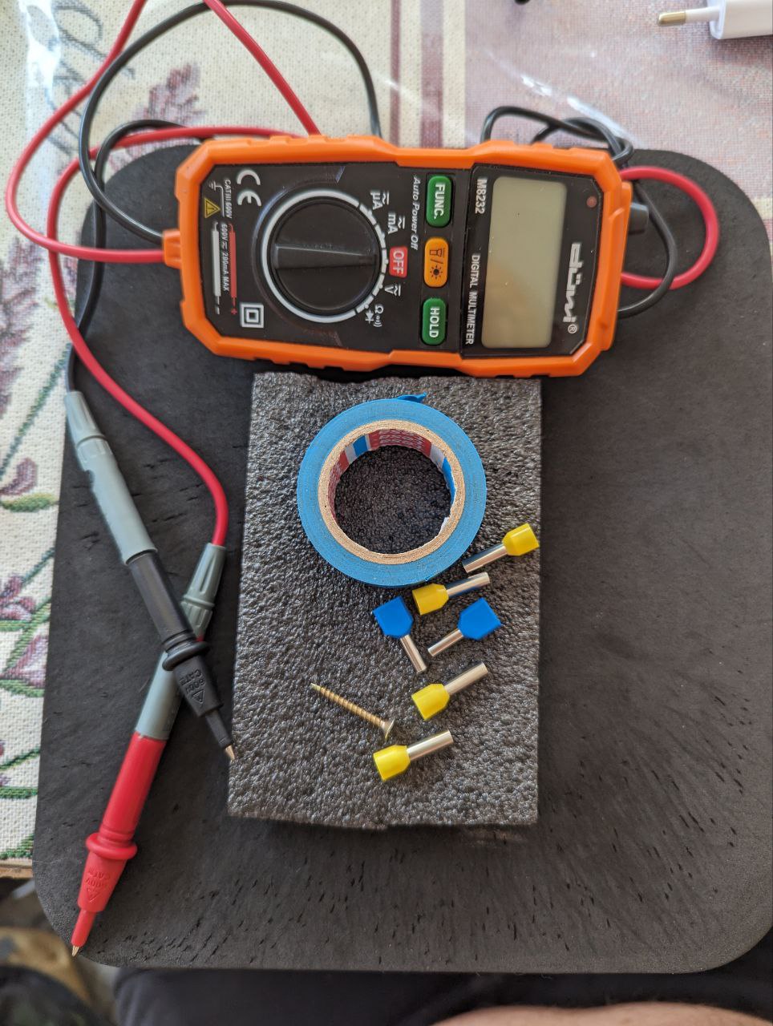
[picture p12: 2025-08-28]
docs/img/etc.jpg

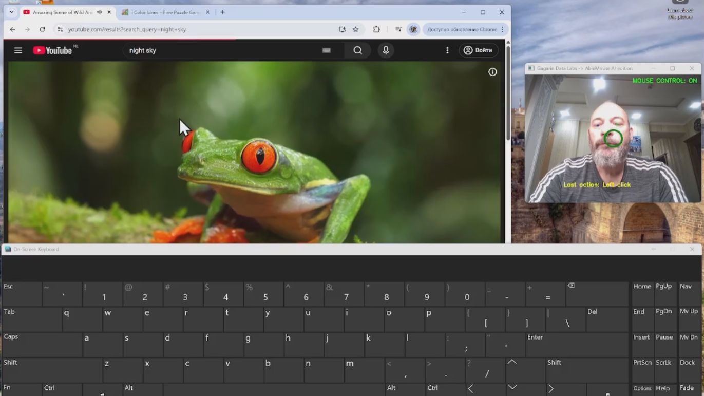
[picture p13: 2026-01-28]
docs/img/ablemouse_ai_screenshot.jpg

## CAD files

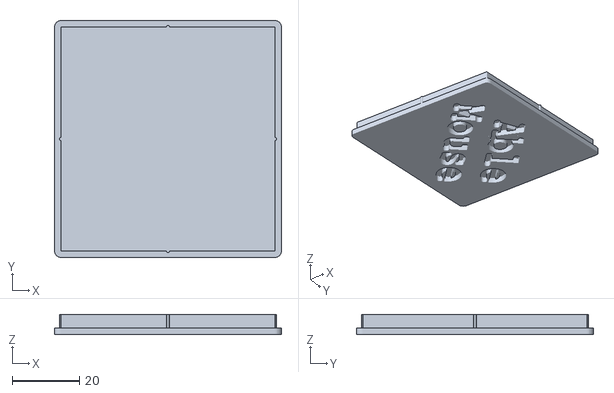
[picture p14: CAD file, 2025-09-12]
3d_printer/models/esp32_box/variations/1/cover.stl
67.5 x 70.5 x 6.00

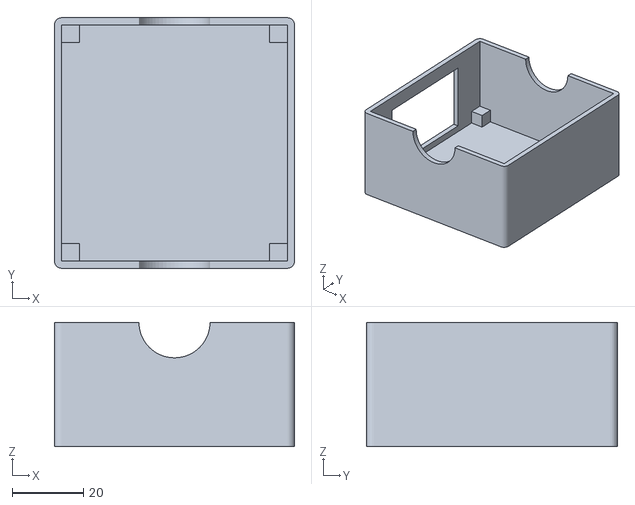
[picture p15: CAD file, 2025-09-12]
3d_printer/models/esp32_box/variations/1/box.stl
67.5 x 70.5 x 35.0

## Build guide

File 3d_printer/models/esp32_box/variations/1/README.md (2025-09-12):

# A case for an ESP32 board and its adapter

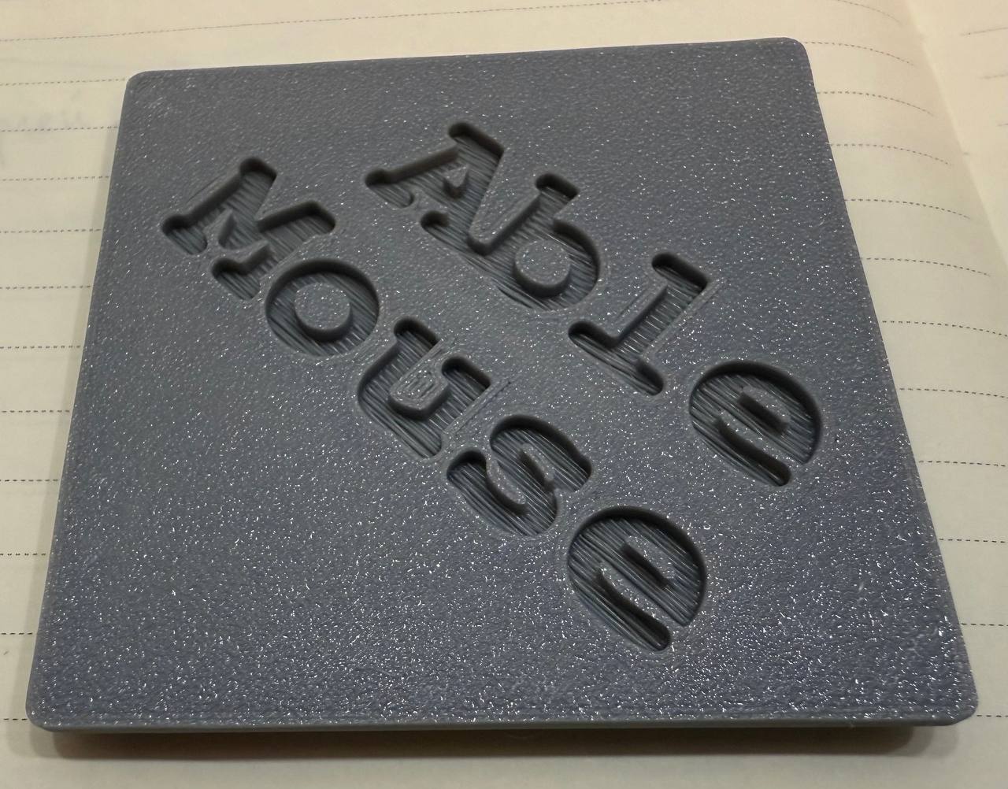
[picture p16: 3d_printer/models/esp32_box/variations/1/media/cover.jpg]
Cover

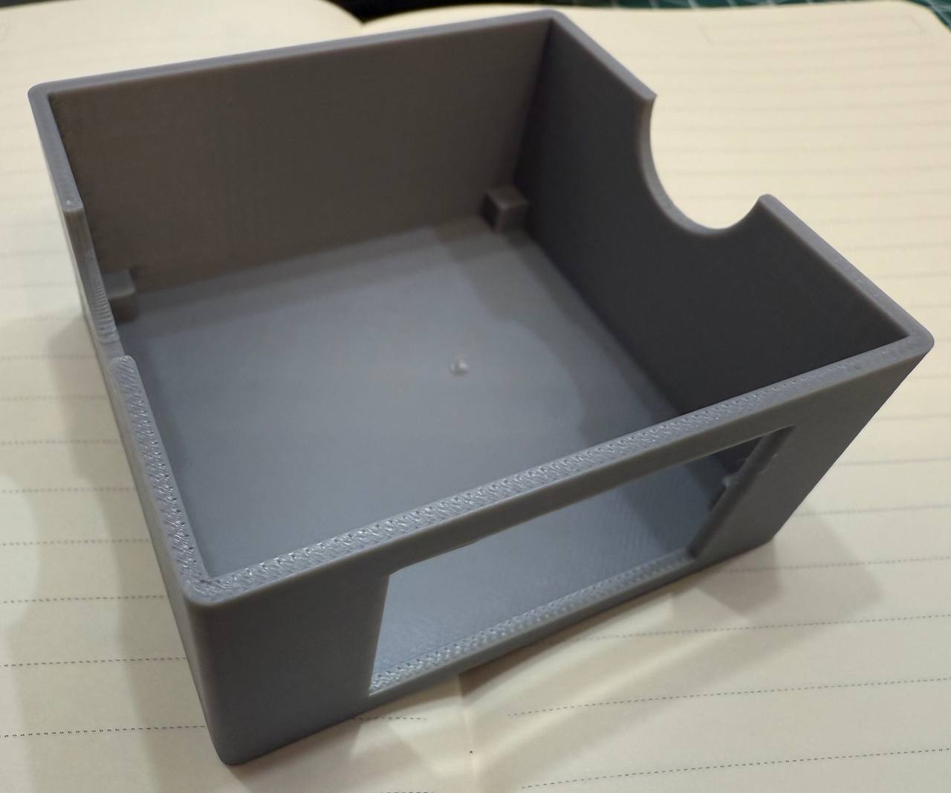
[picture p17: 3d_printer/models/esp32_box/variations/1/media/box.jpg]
Box

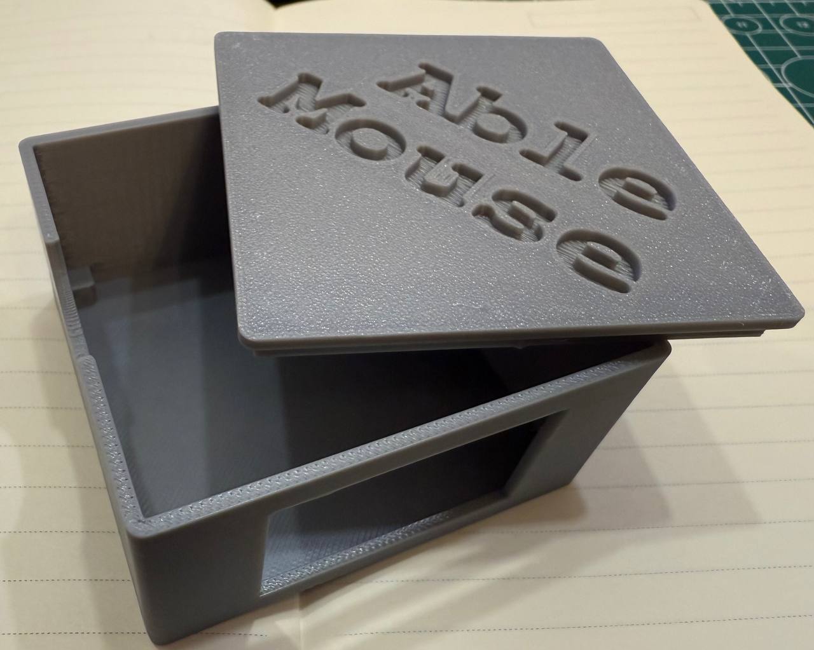
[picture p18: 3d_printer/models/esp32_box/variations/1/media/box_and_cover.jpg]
Cover&Box


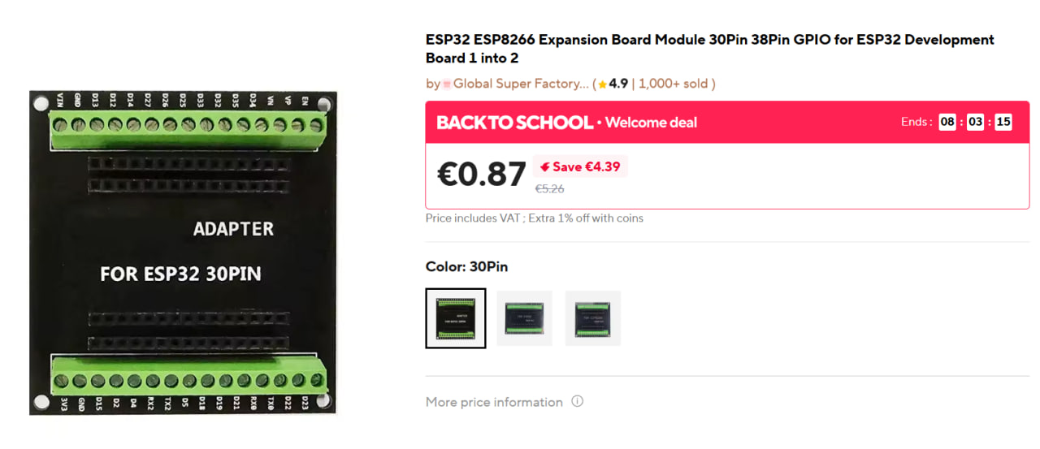
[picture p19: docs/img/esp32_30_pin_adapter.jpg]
ESP32 Adapter

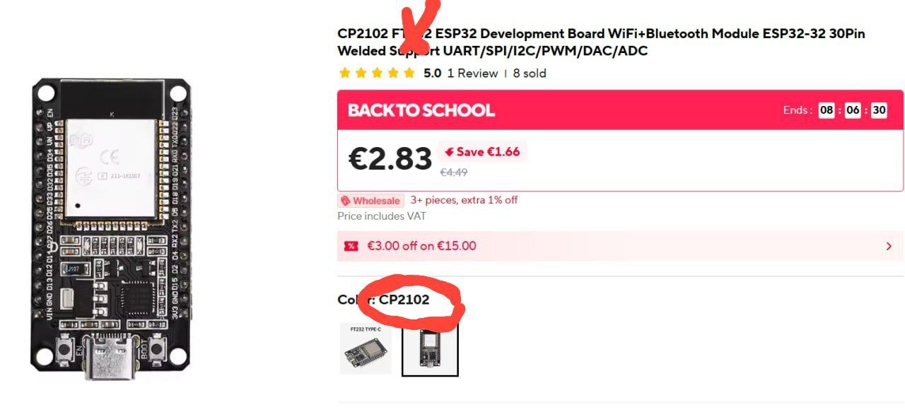
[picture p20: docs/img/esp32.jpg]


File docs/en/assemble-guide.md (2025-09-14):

# AbleMouse. Assemble Guide.
> This guide will be updated as questions, ideas, or new implementations are contributed by the community.

This guide will help you assemble a touch-controlled device

## Table of Contents
1. [Components Needed](#components-needed)
2. [Assembly Instructions](#assembly-instructions)
3. [Software Setup](#software-setup)
4. [Final Assembly for the User](#device-configuration)
5. [Usage](#usage)

## Components Needed

### Main Components
> **Note:** The links provided are examples. You can source the components locally or from any supplier of your choice.

---

#### 1.1 ESP32 CP2102 DevKit with Wi-Fi and Bluetooth
You need a 30-pin ESP32 development board (DevKit v1).

ESP32 Board

Example: [AliExpress link](https://www.aliexpress.com/item/1005008684478950.html)

#### 1.2 Dupont Wire Assorted Kit Male to Male
10-15 cm length is sufficient.

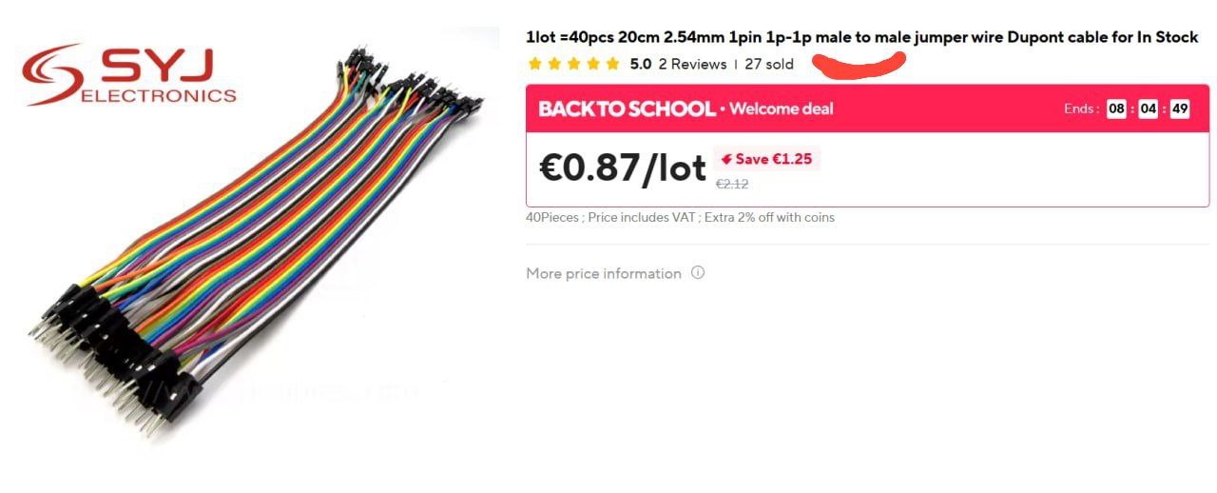
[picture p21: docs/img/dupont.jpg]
Dupont Wires


Example: [AliExpress link](https://www.aliexpress.com/item/33027115346.html)

#### 1.3 Breadboard Options

##### Option 1: 400 Hole Breadboard
You will need to cut it in half lengthwise as ESP32 pins won't align perfectly.

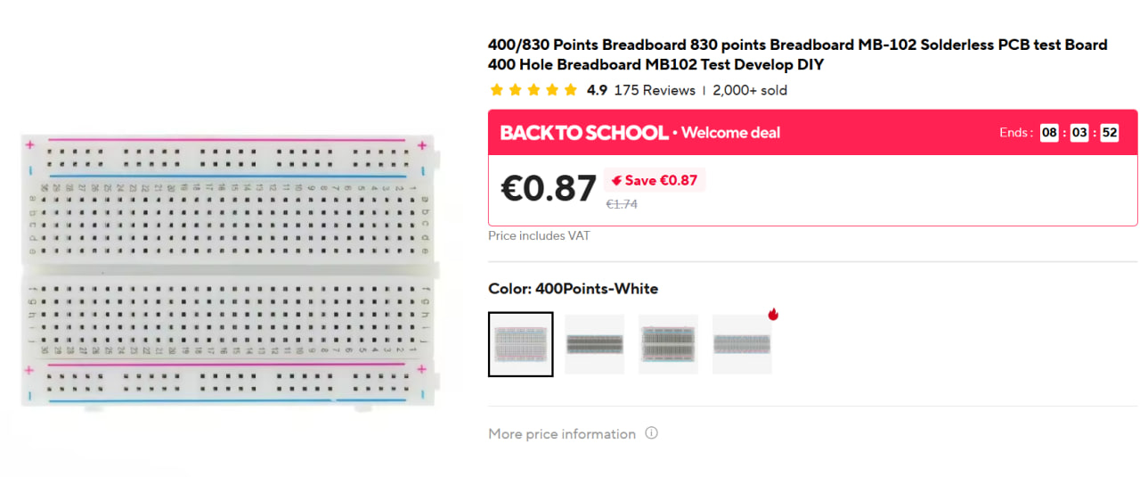
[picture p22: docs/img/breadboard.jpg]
Breadboard


Example: [AliExpress link](https://www.aliexpress.com/item/1005007085965483.html)

##### Option 2: ESP32 Terminal Adapter 30pin
ESP32 Adapter

Example: [AliExpress link](https://www.aliexpress.com/item/1005007171930314.html)

#### 1.4 Alligator Clips Double-ended Test Leads
48cm/18.9inch length.

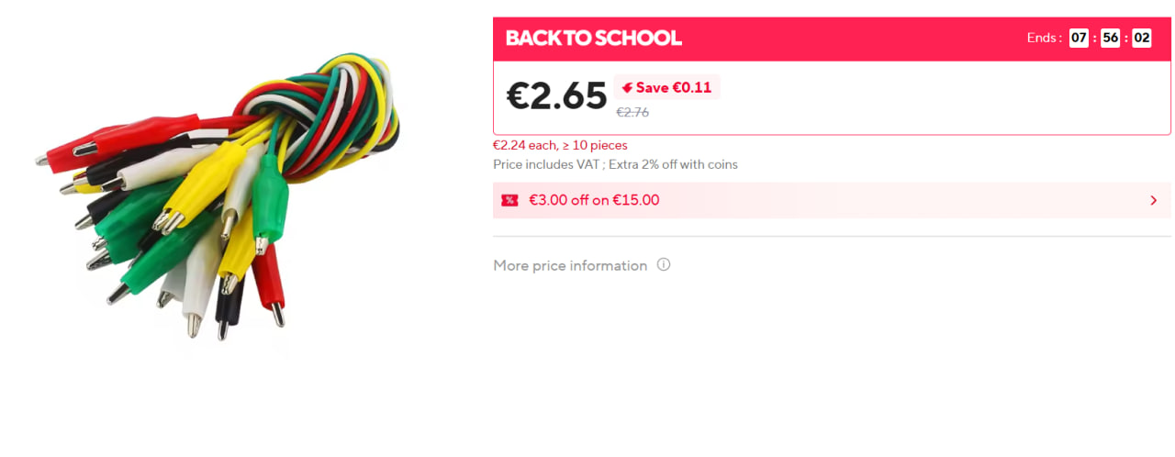
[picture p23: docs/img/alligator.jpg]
Alligator Clips


Example: [AliExpress link](https://www.aliexpress.com/item/4000133770986.html)

> **Note:**  
> - For **tongue control**, this length is sufficient.  
> - For **pedals** (e.g., for users with cerebral palsy), adjust the length based on placement and user needs.

> **Note 2:**  
> If you have soldering skills, you can use flexible stranded wires of your desired length instead.

## Assembly Instructions

### 2.1 ESP32 Pin Specification
Refer to the ESP32 30-pin specification. We're interested in touch-sensitive pins.

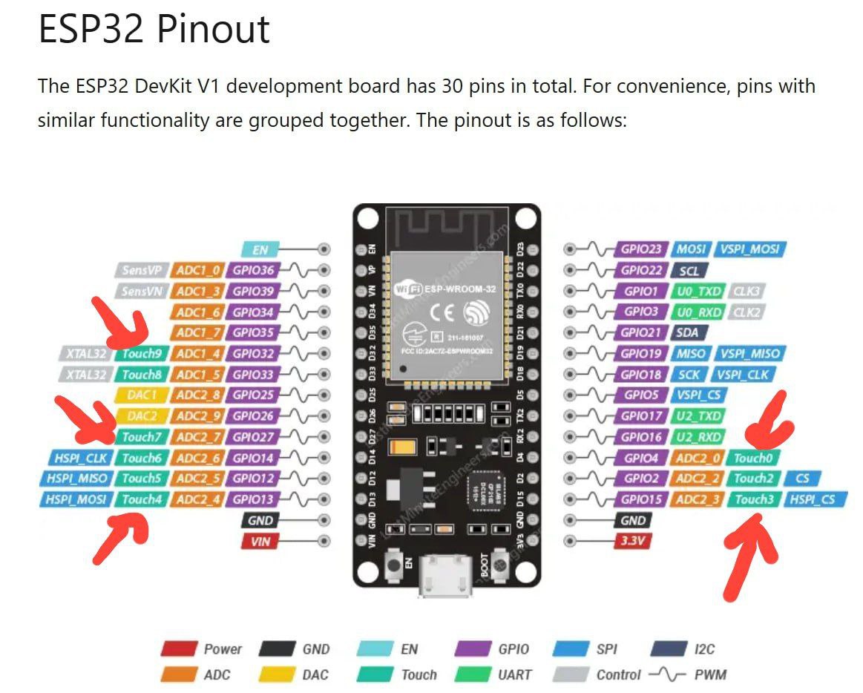
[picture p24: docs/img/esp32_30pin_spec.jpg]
ESP32 Pinout


Reference: [Last Minute Engineers ESP32 Pinout](https://lastminuteengineers.com/esp32-pinout-reference/)

### 2.2 Connect Components
Place the ESP32 on the breadboard or adapter and connect wires to the following pins:
Place the ESP32 on your breadboard (or adapter) and connect the Dupont wires to the following GPIO pins:

| Function        | ESP32 Pin |
|-----------------|---------|
| Move Left       | D4 (GPIO4)  |
| Move Right      | D15 (GPIO15)|
| Move Up         | D33 (GPIO33)|
| Move Down       | D27 (GPIO27)|
| Left Click      | D13 (GPIO13)|
| Right Click     | D32 (GPIO32)|

*Note: to control (MacOS/Windows), four direction keys are sufficient. Click buttons allow faster interaction*

### 2.3 Prototype
At this stage, you should have a working prototype with wires connected to the correct pins.

## Software Setup

### 3.1 Install Programming Software

#### 3.1.1 Download Arduino IDE
Download from: [arduino.cc/en/software/](https://www.arduino.cc/en/software/)

#### 3.1.2 Add ESP32 Support
Follow instructions at: [ESP32 Arduino Installation Guide](https://docs.espressif.com/projects/arduino-esp32/en/latest/installing.html)

#### 3.1.3 Install CP210x Drivers
Download from: [Silicon Labs CP210x Drivers](https://www.silabs.com/software-and-tools/usb-to-uart-bridge-vcp-drivers)

*Windows users need Universal Windows Driver*

#### 3.1.4 Connect ESP32 to Computer
Use USB cable for both power and data transfer.

#### 3.1.5 Select Board
In Arduino IDE, select "ESP32 Dev Module"

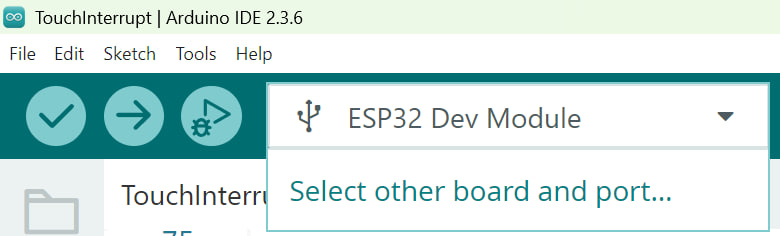
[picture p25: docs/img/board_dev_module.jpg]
Board Selection


### 3.2 Test with Example Code

#### 3.2.1 Touch Test
Copy contents of [`touch_test_GPIO_4.ino`](../../src/esp32/touch_test_GPIO_4.ino) to a new sketch and upload.
If you encounter errors:
> **Troubleshooting:**
> - **Upload fails?** Ensure the USB cable supports data transfer.
> - **Compilation error with `std::string` → `String`?**  
>   This is due to a breaking change in ESP32 Arduino core v3.0.0.  
>   **Solution:** Downgrade to **ESP32 core v2.0.17** via Boards Manager.  
>   Full guide: [https://forum.arduino.cc/t/ble-mouse-example-compilation-error/1265845](https://forum.arduino.cc/t/ble-mouse-example-compilation-error/1265845)

If upload successful, you'll see messages in Serial Monitor.
Set **Tools → Serial Monitor**. Set baud rate to **115200**.

Touch the wire connected to **D4**. You should see `Touch` in the Serial Monitor.  
If so, the touch sensing is working.

#### 3.2.2 Minimal Touch Example
Copy contents of [`touch_minimal.ino`](../../src/esp32/touch_minimal.ino) to a new sketch and upload.

Open Serial Monitor at 115200 baud rate. Touch the connected wires to see corresponding messages.

Adjust `threshold` variable for sensitivity and `moveSpeed` for mouse movement speed.

##  Final Assembly for the User

### 4.1 Create Touch Panels for People with Motor Disabilities
Connect ESP32 wires to conductive surfaces (e.g., wood wrapped in foil). You can create multiple touch panels.

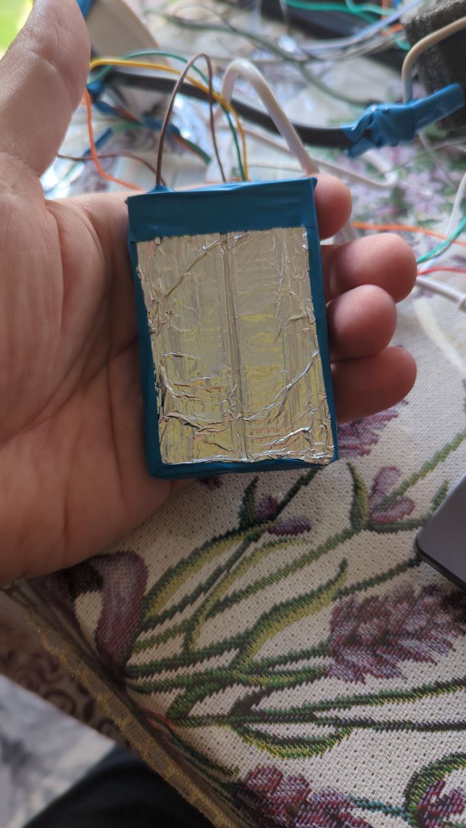
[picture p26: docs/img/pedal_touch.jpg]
Pedal Touch


### 4.2 Tongue Control Interface
Experiment with placement and mounting suitable for the individual user. Some recommendations:

- Position blue contact areas to avoid accidental right/left clicks
- Set contact pads about 1mm below the edge to minimize false triggers
- Use foam for prototyping and experimenting
- Avoid permanent fixation at first; allow for adjustments

>Note: ESP32 touch pins are safe for human interaction because they use a low-power capacitive sensing method that detects changes in electrical capacitance, not direct electrical current. When you touch a connected conductive surface, your body's electrical charge alters the capacitance of the circuit, which the ESP32 reads, but there is no direct electrical connection or significant current flow through the pin to the user. But if you have any considerations you can cover the contact surface with a thin dielectric layer (0.1–0.3 mm), e.g. a common food-grade plastic bag. Note that not all dielectric materials transmit the electric field (this is distinct from electric current). The principle is kind of similar to how touchscreens work through a glass layer. But adjust the sensitivity threshold for your material — touches will be less sensitive. 

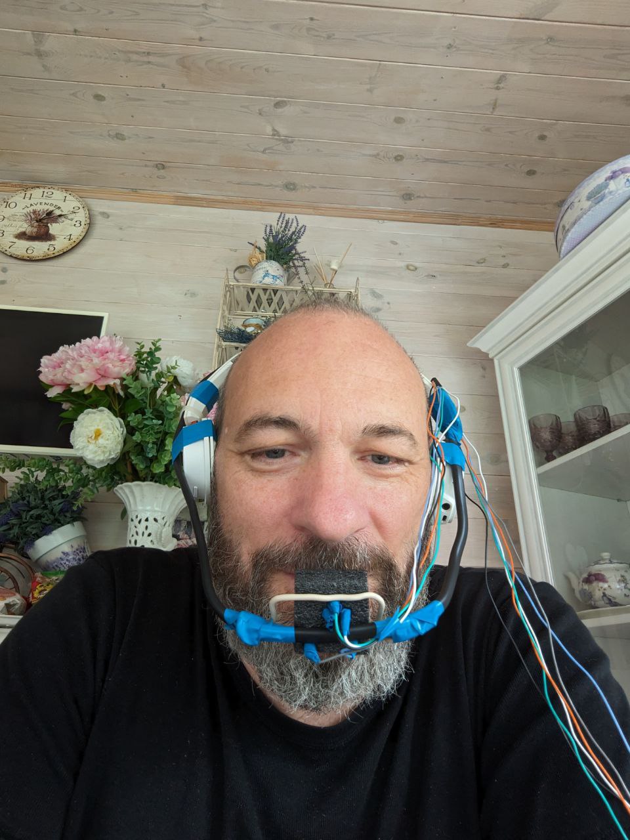
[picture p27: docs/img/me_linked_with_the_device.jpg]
Tongue Device

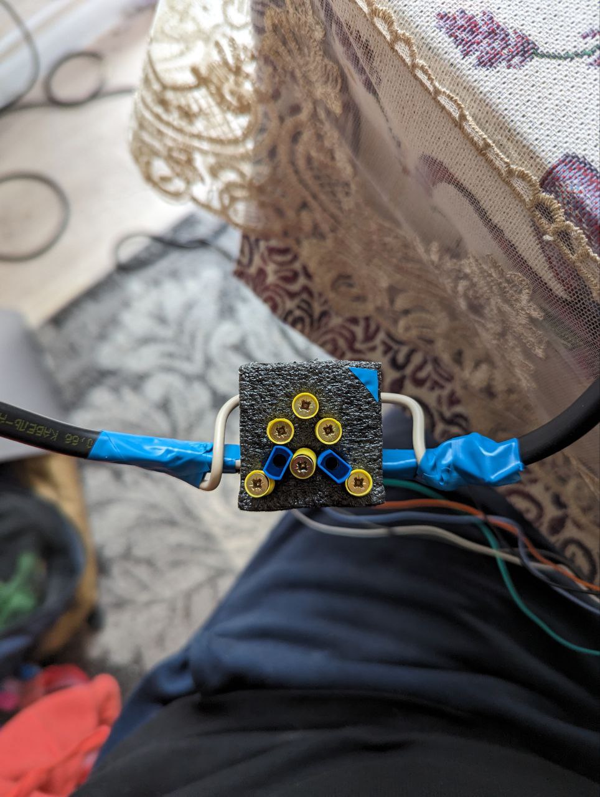
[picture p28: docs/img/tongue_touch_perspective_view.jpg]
Tongue Perspective

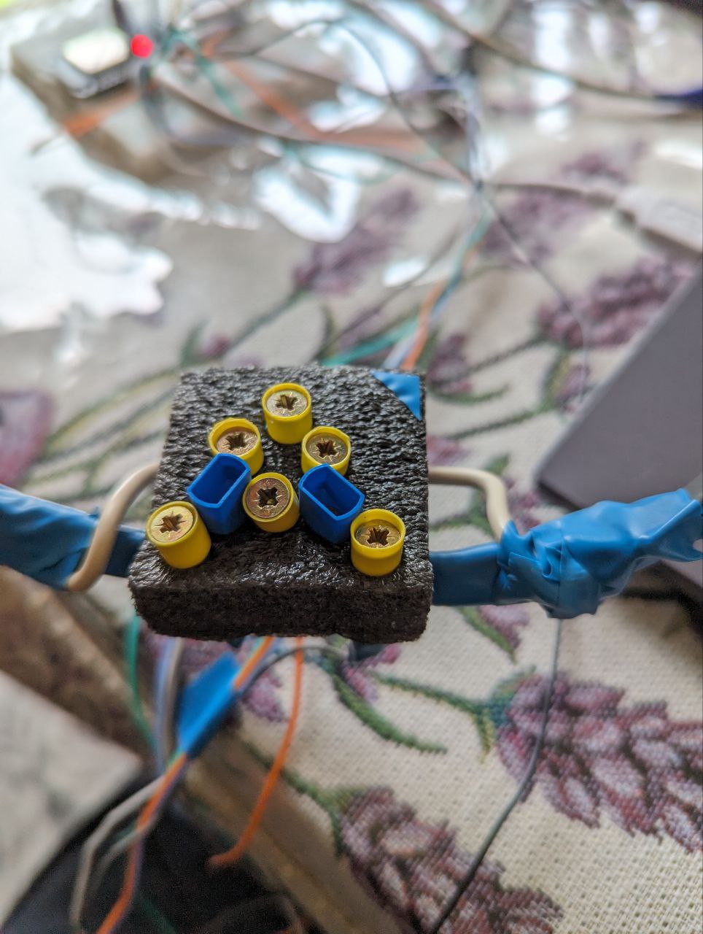
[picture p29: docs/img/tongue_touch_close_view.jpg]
Tongue Closeup

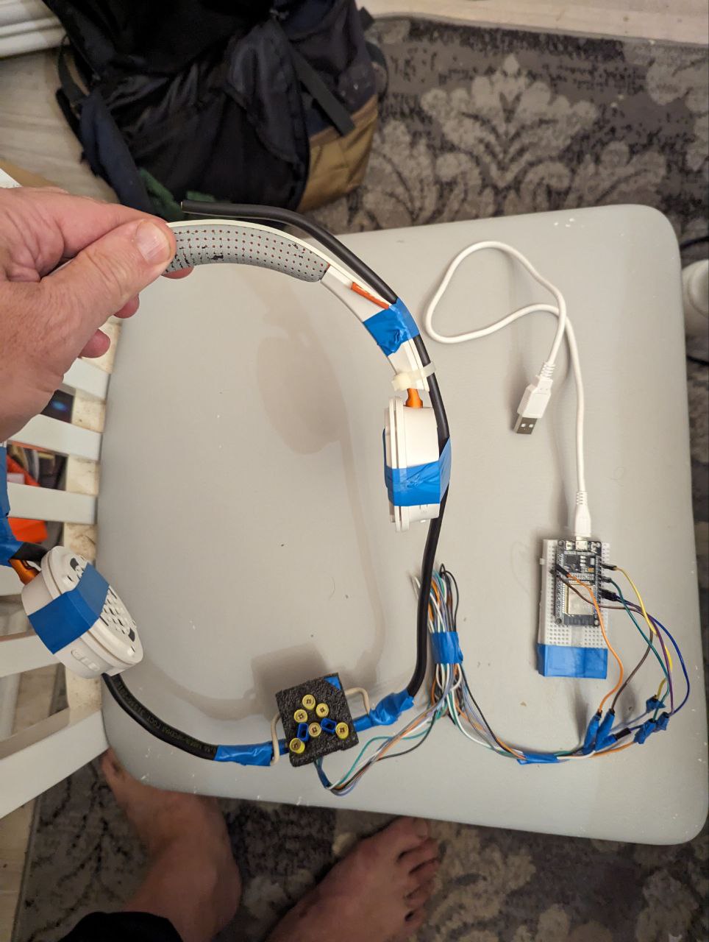
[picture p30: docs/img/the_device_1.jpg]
Device 1

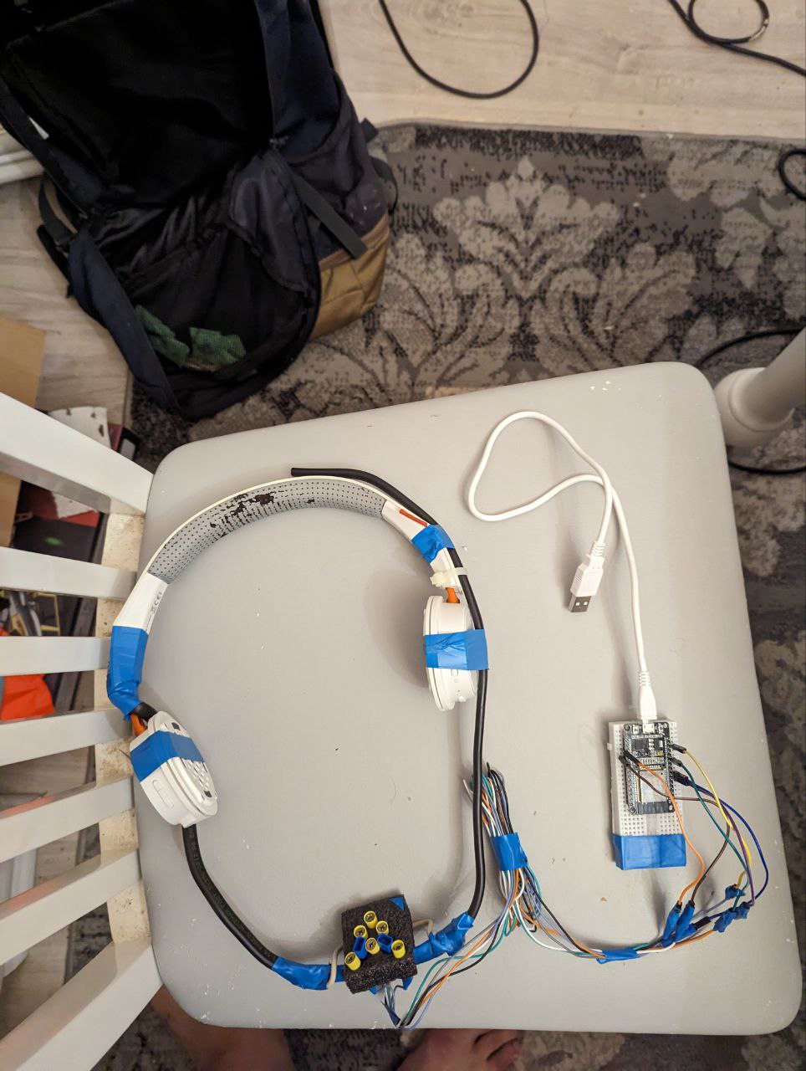
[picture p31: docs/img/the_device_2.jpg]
Device 2

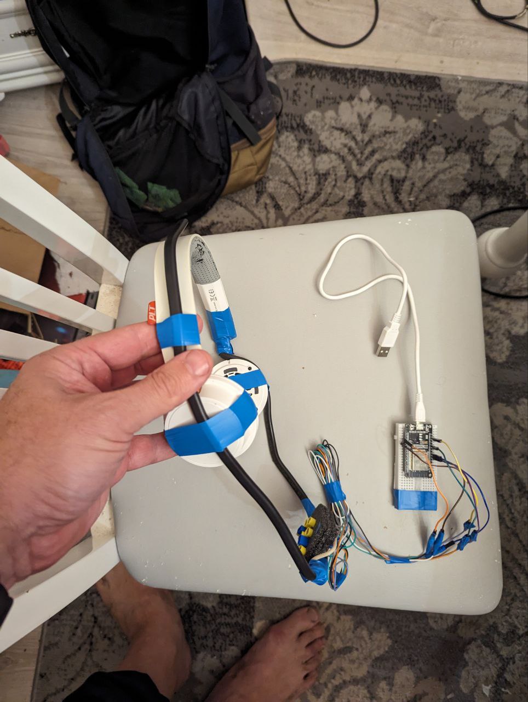
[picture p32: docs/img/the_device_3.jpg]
Device 3

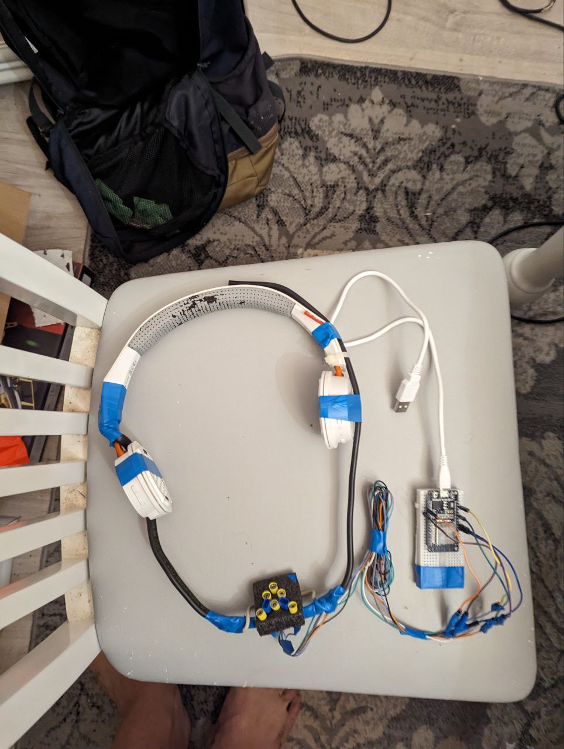
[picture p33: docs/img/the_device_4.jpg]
Device 4


## Usage

### 5.1 Power and Operation
- Power via USB or power bank (not exceeding 5V)
- The last uploaded program runs automatically on power-up
- No need to reprogram each time

### 5.2 Bluetooth Connection
- In computer settings, find and connect to "esp-32" Bluetooth device
- Touch contacts will now control mouse movement

### 5.3 Platform Support
- Built-in accessibility features in MacOS and Windows provide computer control
- Android requires additional software for full gesture support

### 5.4 Training
- For me adaptation time took about 20 minutes
- The tongue is a sensitive muscle that adapts well to the interface
- Individual adaptation time may vary

## Advanced Options

### 6.1 Speed Control Without Reprogramming
Example file: [`touch_minimal_plus_speed_control.ino`](../../src/esp32/touch_minimal_plus_speed_control.ino)

You can implement your own control scheme using physical buttons instead of touch pins.

> This guide will be updated as questions, ideas, or new implementations are contributed by the community.

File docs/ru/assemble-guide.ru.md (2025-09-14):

#  AbleMouse. Руководство по сборке

Это руководство поможет вам собрать устройство на основе ESP32, которое позволяет управлять курсором мыши даже если вы можете шевелить только языком. Устройство предназначено для помощи людям с ограниченными моторными функциями.

>Это руководство будет дополняться и уточняться по мере поступления вопросов и новых идей от сообщества.
---

## 1. Необходимые компоненты

*Примечание: ссылки приведены для примера. Вы можете найти аналогичные компоненты в вашей стране.*

### 1.1. Плата разработчика ESP32
Плата ESP32 DevKit с чипом CP2102, с Wi-Fi и Bluetooth. Достаточно платы с 30 контактами (pin).
*Пример: [AliExpress](https://www.aliexpress.com/item/1005008684478950.html)*
ESP32 DevKit

### 1.2. Провода "папа-папа" (Dupont)
Набор разноцветных проводов типа Male-to-Male длиной 10-15 см.
*Пример: [AliExpress](https://www.aliexpress.com/item/33027115346.html)*
Провода Dupont

### 1.3. Площадка для монтажа (выберите один вариант)

#### Вариант A: Макетная плата (Breadboard)
Макетная плата на 400 отверстий.
*Примечание: стандартную плату, придется распилить вдоль пополам, так как ножки ESP32 не совпадут с отверстиями.*
*Пример: [AliExpress](https://www.aliexpress.com/item/1005007085965483.html)*
Макетная плата

#### Вариант B: Адаптер для ESP32
Готовая плата-адаптер для ESP32 на 30 pin, избавляющая от необходимости использовать и пилить breadboard.
*Пример: [AliExpress](https://www.aliexpress.com/item/1005007171930314.html)*
Адаптер для ESP32

### 1.4. Провода с зажимами "крокодил"
Двусторонние зажимы-крокодилы для создания контактных площадок.
*Примечание: Длины 48 см достаточно для управления языком. Если вы планируете делать педали (например, для рук), длина проводов будет зависеть от конкретного расположения элементов относительно доступных частей тела конкретного человека.*
*Пример: [AliExpress](https://www.aliexpress.com/item/4000133770986.html)*
*Альтернатива: если у вас есть навыки пайки, вы можете использовать просто мягкие провода нужной длины.*
Провода с зажимами

---

## 2. Сборка электрической схемы

### 2.1. Распиновка ESP32
Нас интересуют пины, чувствительные к касанию (Touch Pins). Картинка ниже показывает расположение пинов на 30-пиновой ESP32.
Распиновка ESP32

### 2.2. Схема подключения
Разместите ESP32 на выбранной площадке из п. 1.3 (макетной плате или адаптере). 
С помощью проводов Dupont (1.2) соедините пины ESP32 и  с проводами-"крокодилами" 1.4 согласно следующей карте:

| Функция         | Пин на ESP32 |
|-----------------|--------------|
| Движение влево  | D4 (TOUCH0)  |
| Движение вправо | D15 (TOUCH3) |
| Движение вверх  | D33 (TOUCH8) |
| Движение вниз   | D27 (TOUCH7) |
| Левый клик      | D13 (TOUCH4) |
| Правый клик     | D32 (TOUCH9) |

*Примечание: Для базового управления достаточно четырех направлений. Левый и правый клик добавляют дополнительные возможности.*

На данном этапе у вас должна получиться собранная электрическая схема, готовая для программирования и тестирования.

---

## 3. Программирование и первичная проверка

### 3.1. Установка необходимого ПО
>Чуть позже переведу текст по ссылкам, чтоб было доступно максимальному количеству людей
1.  **Скачайте и установите Arduino IDE**: https://www.arduino.cc/en/software/
2.  **Добавьте поддержку ESP32 в Arduino IDE**: следуйте официальной инструкции https://docs.espressif.com/projects/arduino-esp32/en/latest/installing.html
3.  **Установите драйверы для CP210x**: скачайте и установите драйверы с официального сайта Silicon Labs https://www.silabs.com/software-and-tools/usb-to-uart-bridge-vcp-drivers (для Windows выберите "Universal Windows Driver").
4.  **Подключите ESP32 к компьютеру** с помощью USB-кабеля (убедитесь, что кабель поддерживает передачу данных, а не только зарядку).
5.  **В Arduino IDE** выберите плату: `Tools` -> `Board` -> `ESP32 Arduino` -> `ESP32 Dev Module`.
Выбор платы

### 3.2. Тестовый скетч (проверка касаний)

1.  Скопируйте код из файла [`touch_test_GPIO_4.ino`](../../src/esp32/touch_test_GPIO_4.ino) в новое окно Arduino IDE.
2.  Нажмите кнопку загрузки (->). Код должен скомпилироваться и загрузиться на плату.
    *   **Если возникли ошибки:**
        *   Убедитесь, что используется правильный USB-порт (`Tools` -> `Port`).
        *   Убедитесь, что кабель передает данные.
        *   Если видите ошибку, связанную с `BleMouse.cpp` (например, `cannot convert 'std::string' to 'String'`), понизьте версию платформы (espressif) ESP32 в Arduino IDE до **2.0.17** (в менеджере плат)
        согласно этой инструкции https://forum.arduino.cc/t/ble-mouse-example-compilation-error/1265845
3.  Откройте `Tools` -> `Serial Monitor`. Установите скорость (Baud Rate) `115200`.
4.  Коснитесь пальцем провода, подключенного к пину `D4`. В мониторе порта должно появиться сообщение `Touch`. Это означает, что плата и сенсорные пины работают корректно.

### 3.3. Основной скетч (эмуляция мыши)

1.  Скопируйте код из файла [`touch_minimal.ino`](../../src/esp32/touch_minimal.ino) в Arduino IDE.
2.  Загрузите его на ESP32.
3.  В Serial Monitor вы увидите сообщения о касаниях соответствующих пинов.
4.  В коде вы можете настроить параметры:
    *   `threshold` - чувствительность сенсорных пинов (чем меньше значение, тем выше чувствительность).
    *   `moveSpeed` - скорость (сколько пикселей смещение за клик) перемещения курсора мыши.

---

## 4. Создание интерфейса для пользователя

Это творческая часть, которая зависит от потребностей конкретного человека.

### 4.1. Вариант: Контактные педали (например, для ладони)
Подсоедините провода с зажимами-"крокодилами" к контактным площадкам. Площадками могут служить, например, еревянные бруски, обмотанные фольгой. Можно создать несколько независимых педалей.
Пример педали

### 4.2. Вариант: Площадка для управления языком
Если вы делаете площадку для управления языком, вам нужно будет поэкспериментировать с расположением и способом крепления — всё зависит от конкретного человека.
Для примера расскажу, как сделал я. Я провёл множество экспериментов и в итоге придумал и реализовал своё решение по расположению и креплению.
Примечание: синие площадки помогают избежать случайного нажатия левой и правой кнопок.
Рекомендую устанавливать контактную площадку в жёлтых направляющих примерно на миллиметр ниже края — это снизит вероятность ложных срабатываний.
Вы можете поэкспериментировать с разной высотой и расположением элементов. Например, в одном из моих вариантов "левая кнопка мыши" размещалась посередине между контактами управления направлением. В таком случае её лучше немного утопить, чтобы её уровень был чуть ниже, чем у контактов направления.
Для создания макета советую использовать поролон — с ним удобнее экспериментировать.
Также рекомендую сначала не фиксировать площадку жёстко — оставьте возможность вносить изменения в процессе настройки.

>Примечание: сенсорные пины (touch pins) ESP32 безопасны для взаимодействия с человеком, поскольку в них используется низкоэнергетический ёмкостный метод sensing, который обнаруживает изменения электрической ёмкости, а не прямой электрический ток.
Когда вы касаетесь подключенной conductive поверхности, электрический заряд вашего тела изменяет ёмкость цепи, что и считывает ESP32. При этом не происходит прямого электрического соединения или значительного протекания тока через пин к пользователю. Однако, если у вас есть какие-либо опасения, Вы можете покрыть контактную поверхность тонким диэлектрическим слоем (0,1–0,3 мм), например, обычным пищевым пластиковым пакетом. Учтите, что не все диэлектрические материалы пропускают электрическое поле (не путать с током). Принцип работы похож на то, как работают сенсорные экраны через стеклянный слой. Но не забудьте настроить порог чувствительности под ваш материал — касания будут менее чувствительными.

Вид сбоку
Крупный план
Готовое устройство 1
Готовое устройство 2
Готовое устройство 3
Готовое устройство 4

---

## 5. Финальная сборка и использование

1.  Соберите окончательную конструкцию, надежно закрепив все компоненты.
2.  Питание можно подать от USB-порта компьютера или от power bank (напряжение не должно превышать 5V).
3.  Включите Bluetooth на целевом устройстве (ПК, Mac, телефон).
4.  Найдите новое устройство `ESP32` и выполните сопряжение.
5.  Курсор мыши начнет двигаться при касании контактов.

*   **Windows/MacOS:** Встроенные функции специальных возможностей позволят полноценно управлять интерфейсом.
*   **Android:** Для полноценного управления может потребоваться установка дополнительного приложения-помощника для жестов мыши.

---

## 6. Дополнительные возможности

Вы можете использовать файл [`touch_minimal_plus_speed_control.ino`](../../src/esp32/touch_minimal_plus_speed_control.ino) для реализации дополнительного контроля скорости прямо с сенсорных площадок без перепрошивки. Это лишь пример — вы можете разработать свою собственную схему управления, используя не только touch-пины, но и, например, физические кнопки.

---

## 7. Обучение и адаптация

В среднем, для адаптации к управлению языком требуется около 20 минут практики. Язык — очень чувствительная и подвижная мышца, которая быстро обучается. Время адаптации индивидуально.

---

>Это руководство будет дополняться и уточняться по мере поступления вопросов и новых идей от сообщества.

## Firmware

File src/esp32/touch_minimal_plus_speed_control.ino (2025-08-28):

#include <BleMouse.h>

/*
 * ESP32 Touch-Controlled BLE Mouse
 *
 * Features:
 * - Touch-based mouse movement (up, down, left, right)
 * - Left and right mouse clicks
 * - Speed control via touch:
 *   • Short press: increase speed by +5
 *   • Long press (1s): decrease speed by -5 (min 1)
 * - Speed changes limited to once per second
 *
 * Pin mapping:
 * D4  - Move left
 * D15 - Move right
 * D33 - Move up
 * D27 - Move down
 * D13 - Left click
 * D32 - Right click
 * D14 - Speed control
 */

 /*
 * ALGORITHM DESCRIPTION / ОПИСАНИЕ АЛГОРИТМА
 *
 * (en):
 *
 * Speed Control Algorithm Logic:
 *
 * Overview:
 * The algorithm implements a touch-based speed control system with short press for speed increase
 * and long press for speed decrease functionality.
 *
 * Key Components:
 * 1. Touch Sensing: Uses filtered touch readings from pin D14 for reliable detection
 * 2. State Machine: Tracks button press/release states and press duration
 * 3. Speed Management: Controls movement speed with cooldown periods
 *
 * Algorithm Flow:
 *
 * 1. Touch Detection:
 *    - Reads touch sensor value from pin D14
 *    - Applies moving average filter (5 samples) for stability
 *    - Compares filtered value against threshold (20) to determine touch state
 *
 * 2. State Tracking:
 *    - speedButtonPressed: Tracks if button is currently pressed
 *    - longPressActive: Flags when long press is detected
 *    - shortPressHandled: Prevents duplicate short press handling
 *
 * 3. Press Detection:
 *    - Button Press: When touch detected and not previously pressed
 *      - Records press start time
 *      - Resets state flags
 *    - Button Release: When touch ends and was previously pressed
 *      - Handles short press (if not already handled)
 *      - Resets all states
 *
 * 4. Long Press Handling:
 *    - After 1000ms of continuous press, activates long press mode
 *    - Decreases speed by 5 every 1000ms while pressed
 *    - Minimum speed limited to 1
 *    - Sets shortPressHandled to prevent short press on release
 *
 * 5. Short Press Handling:
 *    - On release before 1000ms, increases speed by 5
 *    - Respects 1000ms cooldown between changes
 *    - Only executed if long press wasn't activated
 *
 * 6. Cooldown Management:
 *    - lastSpeedChangeTime ensures minimum 1 second between speed changes
 *    - Prevents rapid consecutive adjustments
 *
 * (ru):
 *
 * Логика алгоритма контроля скорости:
 *
 * Обзор:
 * Алгоритм реализует сенсорную систему контроля скорости с коротким нажатием для увеличения скорости
 * и длинным нажатием для уменьшения.
 *
 * Ключевые компоненты:
 * 1. Сенсорное управление: Использует фильтрованные показания с пина D14 для надежного определения
 * 2. Конечный автомат: Отслеживает состояния нажатия/отпускания и длительность нажатия
 * 3. Управление скоростью: Контролирует скорость перемещения с периодами задержки
 *
 * Логика работы:
 *
 * 1. Обнаружение касания:
 *    - Чтение значения сенсора с пина D14
 *    - Применение скользящего среднего (5 samples) для стабильности
 *    - Сравнение отфильтрованного значения с порогом (20)
 *
 * 2. Отслеживание состояний:
 *    - speedButtonPressed: Отслеживает текущее состояние нажатия
 *    - longPressActive: Флаг длинного нажатия
 *    - shortPressHandled: Предотвращает повторную обработку короткого нажатия
 *
 * 3. Обнаружение нажатий:
 *    - Нажатие кнопки: При обнаружении касания
 *      - Запись времени начала нажатия
 *      - Сброс флагов состояний
 *    - Отпускание кнопки: При окончании касания
 *      - Обработка короткого нажатия (если не обработано)
 *      - Сброс всех состояний
 *
 * 4. Обработка длинного нажатия:
 *    - После 1000ms непрерывного нажатия активирует режим длинного нажатия
 *    - Уменьшает скорость на 5 каждые 1000ms пока нажато
 *    - Минимальная скорость ограничена значением 1
 *    - Устанавливает shortPressHandled для предотвращения короткого нажатия
 *
 * 5. Обработка короткого нажатия:
 *    - При отпускании до 1000ms увеличивает скорость на 5
 *    - Соблюдает задержку 1000ms между изменениями
 *    - Выполняется только если не было длинного нажатия
 *
 * 6. Управление задержками:
 *    - lastSpeedChangeTime обеспечивает минимум 1 секунду между изменениями скорости
 *    - Предотвращает быстрое последовательное изменение скорости
 *
 * Преимущества алгоритма:
 * - Устойчивость к "дребезгу" сенсора благодаря фильтрации
 * - Четкое разделение коротких и длинных нажатий
 * - Защита от случайных multiple-triggers
 * - Плавное и предсказуемое управление скоростью
 */


BleMouse bleMouse("ESP32-Touch-Mouse");

int threshold = 10; // Increased threshold for better stability
int moveSpeed = 5; // Base movement speed

// Touch detection flags
bool touchLeftDetected = false;    // D4 - left
bool touchRightDetected = false;   // D15 - right
bool touchUpDetected = false;      // D33 - up
bool touchDownDetected = false;    // D27 - down
bool touchLeftClickDetected = false;  // D13 - left click
bool touchRightClickDetected = false; // D32 - right click

// Speed control variables
unsigned long lastSpeedChangeTime = 0;
const unsigned long speedChangeCooldown = 1000; // Cooldown between speed changes
bool speedButtonPressed = false;
unsigned long speedButtonPressTime = 0;
const unsigned long longPressDuration = 1000; // Long press duration
bool longPressActive = false;
bool shortPressHandled = false;

// Touch value filtering
const int FILTER_SAMPLES = 5;
int touchReadings[FILTER_SAMPLES];
int readIndex = 0;
int touchTotal = 0;
int touchAverage = 0;

void handleTouchLeft() {
  touchLeftDetected = true;
}

void handleTouchDown() {
  touchDownDetected = true;
}

void handleTouchRight() {
  touchRightDetected = true;
}

void handleTouchLeftClick() {
  touchLeftClickDetected = true;
}

void handleTouchUp() {
  touchUpDetected = true;
}

void handleTouchRightClick() {
  touchRightClickDetected = true;
}

void setup() {
  Serial.begin(115200);
  delay(1000);
  Serial.println("ESP32 Touch Mouse Started");
  Serial.print("Initial move speed: ");
  Serial.println(moveSpeed);

  // Initialize touch filter
  for (int i = 0; i < FILTER_SAMPLES; i++) {
    touchReadings[i] = touchRead(14);
    touchTotal += touchReadings[i];
  }
  touchAverage = touchTotal / FILTER_SAMPLES;

  // Assign touch interrupt handlers
  touchAttachInterrupt(4, handleTouchLeft, threshold);        // LEFT
  touchAttachInterrupt(27, handleTouchDown, threshold);       // DOWN
  touchAttachInterrupt(15, handleTouchRight, threshold);      // RIGHT
  touchAttachInterrupt(13, handleTouchLeftClick, threshold);  // LEFT CLICK
  touchAttachInterrupt(33, handleTouchUp, threshold);         // UP
  touchAttachInterrupt(32, handleTouchRightClick, threshold); // RIGHT CLICK

  bleMouse.begin();
  Serial.println("BLE Mouse started");
}

int getFilteredTouchValue() {
  // Remove the oldest reading
  touchTotal -= touchReadings[readIndex];

  // Read new value
  touchReadings[readIndex] = touchRead(14);

  // Add new value to total
  touchTotal += touchReadings[readIndex];

  // Update index
  readIndex = (readIndex + 1) % FILTER_SAMPLES;

  // Return average
  return touchTotal / FILTER_SAMPLES;
}

void handleSpeedControl() {
  unsigned long currentTime = millis();

  // Get filtered touch value
  int filteredTouch = getFilteredTouchValue();
  bool isTouched = (filteredTouch < threshold);

  if (isTouched && !speedButtonPressed) {
    // Button just pressed
    speedButtonPressed = true;
    speedButtonPressTime = currentTime;
    longPressActive = false;
    shortPressHandled = false;
    Serial.print("Speed button pressed, value: ");
    Serial.println(filteredTouch);
  }
  else if (!isTouched && speedButtonPressed) {
    // Button released
    if (!longPressActive && !shortPressHandled) {
      // Short press - increase speed
      if (currentTime - lastSpeedChangeTime >= speedChangeCooldown) {
        moveSpeed += 5;
        lastSpeedChangeTime = currentTime;
        shortPressHandled = true;
        Serial.print("Speed increased: ");
        Serial.println(moveSpeed);
      }
    }
    speedButtonPressed = false;
    longPressActive = false;
    Serial.println("Speed button released");
  }
  else if (isTouched && speedButtonPressed) {
    // Button still pressed
    unsigned long pressDuration = currentTime - speedButtonPressTime;

    if (!longPressActive && pressDuration >= longPressDuration) {
      // Long press detected
      longPressActive = true;
      shortPressHandled = true; // Prevent short press handling
      Serial.println("Long press detected");
    }

    // Continuous speed decrease during long press
    if (longPressActive && (currentTime - lastSpeedChangeTime >= speedChangeCooldown)) {
      moveSpeed = max(1, moveSpeed - 5);
      lastSpeedChangeTime = currentTime;
      Serial.print("Speed decreased: ");
      Serial.println(moveSpeed);
    }
  }
}

void loop() {
  // Handle speed control
  handleSpeedControl();

  // Handle movement
  if (touchLeftDetected) {
    bleMouse.move(-moveSpeed, 0);
    Serial.print("Moving LEFT, speed: ");
    Serial.println(moveSpeed);
  }

  if (touchRightDetected) {
    bleMouse.move(moveSpeed, 0);
    Serial.print("Moving RIGHT, speed: ");
    Serial.println(moveSpeed);
  }

  if (touchUpDetected) {
    bleMouse.move(0, -moveSpeed);
    Serial.print("Moving UP, speed: ");
    Serial.println(moveSpeed);
  }

  if (touchDownDetected) {
    bleMouse.move(0, moveSpeed);
    Serial.print("Moving DOWN, speed: ");
    Serial.println(moveSpeed);
  }

  if (touchLeftClickDetected) {
    bleMouse.click(MOUSE_LEFT);
    Serial.println("Single left click");
  }

  if (touchRightClickDetected) {
    bleMouse.click(MOUSE_RIGHT);
    Serial.println("Single right click");
    delay(100);
  }

  // Reset touch flags
  touchLeftDetected = false;
  touchRightDetected = false;
  touchDownDetected = false;
  touchLeftClickDetected = false;
  touchUpDetected = false;
  touchRightClickDetected = false;

  delay(50); // Slightly longer delay for stability
}

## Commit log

2025-08-27 🚧 Page in progress — will complete it by the end of August 2025
2025-08-27 Update README.ru.md 🚧 Page in progress — will complete it by the end of August 2025
2025-08-28 en assembly guide
2025-08-28 README.md 🚧 Page in progress - removed
2025-09-10 fix: 中国人 to 中文
2025-09-12 3D model: A case for an ESP32 board and its adapter
    [box.stl, cover.stl]
2025-09-14 move esp32 src to dedicated dir
2025-09-15 fix link to mouse_сommander.ahk
2026-02-19 talk2cam добавлен режим «один снимок после отправки инструкции».
    Что изменилось
    - В блоке «Instruction» появился чекбокс One-shot on Send.
    - Когда этот режим включён, при нажатии на кнопку Send:
    - Инструкция обновляется.
    - Делается один снимок с камеры и тут же отправляется на сервер.
    - Если режим выключен, поведение прежнее:
    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
2026-02-20 добавлен встроенный медиапроигрыватель в интерфейс talk2cam и размещён под окном с камерой.
    Что сделано
    - Встроен мониторинг папки cfg.WATCH_DIR на новые файлы с расширением cfg.WATCH_FILTER.
    - Новые медиафайлы проверяются на «готовность» и воспроизводятся по порядку.
    - Воспроизведение идёт внутри приложения — под превью камеры, в блоке «Media».
    - Поддержаны параметры из cfg_helper.py: масштаб, задержки, о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
2026-02-20 Готово: добавлена опция в talk2cam, которая отправляет текст ответа модели в TTS и запускает генерацию mp4-аватара
    Что добавлено
    - Чекбокс Avatar в верхней панели справа. Если включен, каждый успешно полученный текст ответа автоматически:
    - Преобразуется в аудио (gTTS по умолчанию).
    - Отправляется на AVATAR API для генерации mp4.
    - Медиаплеер уже встроен под окном камеры; готовые mp4 будут появляться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
2026-02-20 добавлена генерация аудио через Microsoft edge-tts по аналогии с tts_google и интегрирована в talk2cam.
    - Новый скрипт tts_edge.py
    - Принимает: text, hash, lang.
    - Использует библиотеку edge-tts для синтеза.
    - Сохраняет файл как {hash}.ogg в cfg.AUDIO_DIR (аналогично текущему пайплайну; поток edge-tts MP3 сохраняется с .ogg для совместимости).
    - Подбор голоса по cfg.EDGE_TTS_VOICE или по языку (ru → ru-RU-SvetlanaNeural, en → en-US-AriaNeural и т.д.).
    -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
2026-02-21 добавлено бесконечное проигрывание matrix.mp4, пока не появится новый файл.
2026-02-22 убраны лишние кнопки добавлена папочка с конфигурацией gbnf
